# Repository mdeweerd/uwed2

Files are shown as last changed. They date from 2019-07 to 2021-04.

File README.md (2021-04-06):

# WARNING

Project not tested.

# INFORMATION

This is based on the open-source project "Open-Source Potentiostat
for Wireless Electrochemical Detection with Smartphones" 
=
See : https://dash.harvard.edu/bitstream/handle/1/37298552/5997382.pdf;jsessionid=20A09C47E57A66C76ECFA98192F31BF9?sequence=1

The reference to "UWED, Alar Ainla, GMW Group Harvard Univ" was left on the PCB.  They did not design this one, but it was adapted from their Eagle Project.

- The wireless module was replaced with an ESP-WROOM-32 because the original module is no longer supported.
- A programming connector was added.
- A THT connector has been added for power.
- A "Battery Management" IC was added to safely charge a Li-Ion/Li-Poly on power connector.
- There was a project to ajust the PAD positions to a Molex/1719730004

And some other "minor" changes as well as an effort to improve the ground plaine.

# SOFTWARE

See ac8b00850_si_002.zip from https://www.ncbi.nlm.nih.gov/pmc/articles/PMC5997382/ to get the original software as well as further information about this project.

The software has to be adapted to the ESP-WROOM-32.

# BUYING COMPONENTS

The original project ensured that all components were available from Digikey.

The `UWED2_proto.xls` file shows where these components were available in 2019.

At that time you would have been able to paste the following list on https://www.digikey.com/ordering/shoppingcart, but the BOM needs to be updated for some passive components and the ESP-WROOM-32 (was: 1904-1010-1-ND):
```csv
2,401-1427-1-ND,BOOT1;EN1
6,490-3340-2-ND,C1;C2;C5;C6;C16;C18
2,311-1136-1-ND,C10;C12
2,399-16641-1-ND,C20;C21
2,1276-1300-1-ND,C3;C4
9,478-1395-1-ND,C7-C9;C11;C13-C15;C17;C19
1,497-18870-1-ND,D7
1,1904-1010-1-ND,IC1
1,AD5667RBRMZ-2-ND,IC2
1,AD8608ARUZ-ND,IC3
2,576-1259-1-ND,IC4;IC5
1,MAX4643EUA+-ND,IC6
1,MAX4644EUT+TCT-ND,IC7
1,LTC2471IMS#PBF-ND,IC8
1,VAOL-S8SB4CT-ND,LED1
1,CP-032HPJCT-ND,P1
1,GH7540CT-ND,P2
1,RR12P1.2KDCT-ND,R1
2,541-4163-1-ND,R11;R12
2,A130132CT-ND,R14;R15
1,311-16.2KCRCT-ND,R2
2,311-845CRCT-ND,R3;R10
1,311-29.4KCRCT-ND,R4
1,311-8.06KCRCT-ND,R5
1,541-4126-1-ND,R7
3,541-4164-1-ND,R8;R9;R13
```

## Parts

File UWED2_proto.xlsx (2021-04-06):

Prj: | UWED.xml |  |  |  |  |  |  |  |  |  |  | Board Qty: | 1
Co.: |  |  |  |  |  |  |  |  |  |  |  | Unit Cost: | €33.98
Prj date: | 21/04/2019 23:56:42 |  |  |  |  |  |  |  |  |  |  | Total Cost: | €33.98 |  |  |  | €23.32 | 19 of 26 parts found |  |  |  | €42.03 | 26 of 26 parts found |  |  |  | €27.24 | 13 of 26 parts found |  |  |  | €36.15 | 23 of 26 parts found |  |  |  | €10.03 | 17 of 26 parts found |  |  |  | €2531.88 | 7 of 26 parts found |  |  |  | €8.20 | 8 of 26 parts found
$ date: | 2019-04-21 23:56:56
Global Part Info |  |  |  |  |  |  |  |  |  |  |  |  |  | Arrow |  |  |  |  | Digi-Key |  |  |  |  | Farnell |  |  |  |  | Mouser |  |  |  |  | Newark |  |  |  |  | Rs Components |  |  |  |  | Tme
Refs | Value | Desc | S1MN | S1PN | S2PN | S2MN | comment | Footprint | Manf | Manf# | Qty | Unit$ | Ext$ | Avail | Purch | Unit$ | Ext$ | Cat# | Avail | Purch | Unit$ | Ext$ | Cat# | Avail | Purch | Unit$ | Ext$ | Cat# | Avail | Purch | Unit$ | Ext$ | Cat# | Avail | Purch | Unit$ | Ext$ | Cat# | Avail | Purch | Unit$ | Ext$ | Cat# | Avail | Purch | Unit$ | Ext$ | Cat#
BOOT1,EN1 | KMR221G LFS | Microminiature SMT Switch |  |  |  |  |  | Buttons_Switches_SMD:SW_SPST_KMR2 | C&K Components | KMR221G LFS (http://www.mouser.com/ds/2/60/kmr2-1109400.pdf) | 2 | €0.20 | €0.40 | 37333 |  | €0.31 | €0.61 | KMR221G LFS (https://octopart.com/click/track?ak=&sig=092a967&sid=1106&ppid=7484007&vpid=473168312&ct=offers) | 93881 | 2 | €0.52 | €1.04 | 401-1427-1-ND (https://octopart.com/click/track?ak=&sig=0c11080&sid=459&ppid=4774225&vpid=34440877&ct=offers) | NonStk |  | €0.37 | €0.73 | 1201424RL (https://octopart.com/click/track?c=1&ak=&sig=0b550e2&sid=819&ppid=7484007&vpid=138698732&ct=offers) | 47995 |  | €0.52 | €1.04 | 611-KMR221G-LFS (https://octopart.com/click/track?ak=&sig=044d06e&sid=2401&ppid=4774225&vpid=476979092&ct=offers) | 3479 |  | €0.20 | €0.40 | 01M8082 (https://octopart.com/click/track?ak=&sig=005da93&sid=2402&ppid=7484007&vpid=11347265&ct=offers) | 2 |  | €1257.49 | €2514.99 | 1359079 (https://octopart.com/click/track?ak=&sig=023d798&sid=10022&ppid=7484007&vpid=445740908&ct=offers)
C1,C2,C5,C6,C16,C18 | 10u | CAP 10u 0805 |  |  |  |  |  | UWED:C0805 | Murata Electronics | GRM219R60J106KE19D (http://datasheet.octopart.com/GRM219R60J106KE19D-Murata-datasheet-10025737.pdf) | 6 | €0.06 | €0.37 | 1250 |  | €0.29 | €1.72 | GRM219R60J106KE19D (https://octopart.com/click/track?ak=&sig=0b1ee93&sid=1106&ppid=196959&vpid=473333448&ct=offers) | NonStk | 6 | €0.06 | €0.37 | 490-3340-2-ND (https://octopart.com/click/track?c=1&ak=&sig=00207e4&sid=459&ppid=196959&vpid=1720932&ct=offers) | NonStk |  | €0.36 | €2.15 | 1845738 (https://octopart.com/click/track?c=1&ak=&sig=07d642b&sid=819&ppid=196959&vpid=139138268&ct=offers) |  |  |  |  |  | NonStk |  |  |  | 13T1205 (https://octopart.com/click/track?c=1&ak=&sig=093089c&sid=2402&ppid=196959&vpid=33412387&ct=offers) |  |  |  |  |  | 19150 |  | €0.29 | €1.77 | GRM219R60J106KE19D (https://octopart.com/click/track?ak=&sig=0f77df8&sid=1532&ppid=196959&vpid=419362567&ct=offers)
C10,C12 | 10n | CAP 10n 0805 |  |  |  |  |  | UWED:C0805 | Yageo | CC0805KRX7R9BB103 (http://datasheet.octopart.com/CC0805KRX7R9BB103-Yageo-datasheet-10883670.pdf) | 2 | €0.03 | €0.06 | 3872 |  | €0.10 | €0.20 | CC0805KRX7R9BB103 (https://octopart.com/click/track?ak=&sig=0ae48fd&sid=1106&ppid=192989&vpid=486423584&ct=offers) | 8428569 | 2 | €0.11 | €0.22 | 311-1136-1-ND (https://octopart.com/click/track?ak=&sig=0c75d82&sid=459&ppid=192989&vpid=115263416&ct=offers) | 82063 |  | €0.06 | €0.12 | 3019937 (https://octopart.com/click/track?ak=&sig=0170063&sid=819&ppid=192989&vpid=508509172&ct=offers) | 1225222 |  | €0.12 | €0.24 | 603-CC805KRX7R9BB103 (https://octopart.com/click/track?ak=&sig=050a8fd&sid=2401&ppid=192989&vpid=115540545&ct=offers) | 13038 |  | €0.15 | €0.30 | 69C9530 (https://octopart.com/click/track?ak=&sig=0896e52&sid=2402&ppid=192989&vpid=115423638&ct=offers) | 28350 |  | €0.06 | €0.11 | 4614013 (https://octopart.com/click/track?ak=&sig=030c7d2&sid=10022&ppid=192989&vpid=229330082&ct=offers) | 249600 |  | €0.03 | €0.06 | CC0805KRX7R9103 (https://octopart.com/click/track?ak=&sig=0c3fc11&sid=1532&ppid=192989&vpid=115817650&ct=offers)
C20,C21 | 1n | CAP 1n 0805 |  |  |  |  |  | UWED:C0805 | KEMET | C0805C102KARACAUTO (http://datasheet.octopart.com/C0805C102KARACAUTO-KEMET-datasheet-104412711.pdf) | 2 | €0.24 | €0.48 | 7575 |  | €0.27 | €0.53 | C0805C102KARACAUTO (https://octopart.com/click/track?ak=&sig=0f82d17&sid=1106&ppid=88181851&vpid=507223026&ct=offers) | 48644 | 2 | €0.24 | €0.48 | 399-16641-1-ND (https://octopart.com/click/track?ak=&sig=09f6ac1&sid=459&ppid=88181851&vpid=459932081&ct=offers) | 3130 |  | €0.24 | €0.48 | 2834506 (https://octopart.com/click/track?ak=&sig=0deef06&sid=819&ppid=88181851&vpid=477257990&ct=offers) | 9930 |  | €0.28 | €0.56 | 80-C0805C102KARAUTO (https://octopart.com/click/track?ak=&sig=051d296&sid=2401&ppid=88181851&vpid=456357008&ct=offers)
C3,C4 | 470p | CAP 470p 0805 |  |  |  |  |  | UWED:C0805 | Samsung Electro-Mechanics | CL21B471KBANNNC (http://datasheet.octopart.com/CL21B471KBANNNC-Samsung-Electro-Mechanics-datasheet-8324245.pdf) | 2 | €0.01 | €0.02 | 1880 |  | €0.09 | €0.19 | CL21B471KBANNNC (https://octopart.com/click/track?ak=&sig=0d22747&sid=1106&ppid=9301762&vpid=486018211&ct=offers) | 212798 | 2 | €0.10 | €0.20 | 1276-1300-1-ND (https://octopart.com/click/track?ak=&sig=0597cd7&sid=459&ppid=9301762&vpid=72526539&ct=offers) |  |  |  |  |  |  |  |  |  |  |  |  |  |  |  | NonStk |  | €0.01 | €0.02 | 7665950 (https://octopart.com/click/track?c=1&ak=&sig=06b5c12&sid=10022&ppid=9301762&vpid=199121410&ct=offers) | 113900 |  | €0.03 | €0.05 | CL21B471KBANNNC (https://octopart.com/click/track?ak=&sig=0ed60ea&sid=1532&ppid=9301762&vpid=88731159&ct=offers)
C7-C9,C11,C13-C15,C17,C19 | 100n | CAP 100n 0805 |  |  |  |  |  | UWED:C0805 | AVX Corporation | 08055C104KAT2A (http://datasheet.octopart.com/08055C104KAT2A-AVX-datasheet-12587061.pdf) | 9 | €0.02 | €0.22 | 2992000 |  | €0.02 | €0.22 | 08055C104KAT2A (https://octopart.com/click/track?ak=&sig=076accc&sid=1106&ppid=55386349&vpid=527050973&ct=offers) | 47595651 | 9 | €0.18 | €1.62 | 478-1395-1-ND (https://octopart.com/click/track?ak=&sig=01b1845&sid=459&ppid=55386349&vpid=187969502&ct=offers) | NonStk |  | €0.18 | €1.59 | 499687 (https://octopart.com/click/track?c=1&ak=&sig=05bafdf&sid=819&ppid=55386349&vpid=202984868&ct=offers) | NonStk |  | €0.19 | €1.71 | 581-08055C104K (https://octopart.com/click/track?c=1&ak=&sig=0e4db2d&sid=2401&ppid=55386349&vpid=187733814&ct=offers) | NonStk |  | €0.19 | €1.71 | 19X2259 (https://octopart.com/click/track?c=1&ak=&sig=090e783&sid=2402&ppid=55386349&vpid=191188899&ct=offers) | 44500 |  | €0.13 | €1.20 | 4646688 (https://octopart.com/click/track?ak=&sig=082b5da&sid=10022&ppid=55386349&vpid=198971583&ct=offers) | NonStk |  | €0.08 | €0.74 | 08055C104KAT2A (https://octopart.com/click/track?ak=&sig=0e9bd19&sid=1532&ppid=55386349&vpid=187735344&ct=offers)
D7 | STPS2L40AF | DIODE SCHOTTKY 40V 2A SMAFLAT |  |  |  |  |  | Diodes_SMD:D_SMA | STMicroelectronics | STPS2L40AF (http://www.jameco.com/Jameco/Products/ProdDS/1538777.pdf) | 1 | €0.15 | €0.15 | 8 |  | €0.37 | €0.37 | STPS2L40AF (https://octopart.com/click/track?ak=&sig=025aeda&sid=1106&ppid=15756178&vpid=473424643&ct=offers) | 10000 | 1 | €0.44 | €0.44 | 497-18870-1-ND (https://octopart.com/click/track?ak=&sig=075f15a&sid=459&ppid=15756178&vpid=533112807&ct=offers) |  |  |  |  |  | 18242 |  | €0.42 | €0.42 | 511-STPS2L40AF (https://octopart.com/click/track?ak=&sig=01766ab&sid=2401&ppid=15756178&vpid=46230308&ct=offers) | 110000 |  | €0.15 | €0.15 | 96AC4092 (https://octopart.com/click/track?ak=&sig=0df9935&sid=2402&ppid=15756178&vpid=530872283&ct=offers)
IC1 | ESP32-WROOM-32 | SMD MODULE, ESP32-D0WDQ6, 32MBIT |  |  |  |  |  | digikey-footprints:ESP32-WROOM-32D | Espressif Systems | ESP32-WROOM-32 (https://www.espressif.com/sites/default/files/documentation/esp32-wroom-32_datasheet_en.pdf) | 1 | €3.80 | €3.80 |  |  |  |  |  | 1498 | 1 | €3.80 | €3.80 | 1904-1010-1-ND (https://octopart.com/click/track?c=1&ak=&sig=04c9fe0&sid=459&ppid=91025511&vpid=475661582&ct=offers) |  |  |  |  |  | 51941 |  | €3.80 | €3.80 | 356-ESP-WROOM-32 (https://octopart.com/click/track?ak=&sig=0026b78&sid=2401&ppid=91025511&vpid=480613118&ct=offers)
IC2 | DAC_AD5667RBRMZ-2 | Dual DAC. 16-bit I2C |  |  |  |  |  | UWED:MSOP10_0.5MM | Analog Devices | AD5667RBRMZ-2 (http://datasheet.octopart.com/AD5667RBRMZ-2-Analog-Devices-datasheet-124928.pdf) | 1 | €9.91 | €9.91 | 66 |  | €9.91 | €9.91 | AD5667RBRMZ-2 (https://octopart.com/click/track?ak=&sig=03ec865&sid=1106&ppid=1256714&vpid=473140498&ct=offers) | 3052 | 1 | €11.15 | €11.15 | AD5667RBRMZ-2-ND (https://octopart.com/click/track?ak=&sig=049c553&sid=459&ppid=1256714&vpid=1403056&ct=offers) | 167 |  | €11.19 | €11.19 | 1498716 (https://octopart.com/click/track?ak=&sig=02575de&sid=819&ppid=1256714&vpid=138551615&ct=offers) | 182 |  | €10.45 | €10.45 | 584-AD5667RBRMZ-2 (https://octopart.com/click/track?ak=&sig=07a096d&sid=2401&ppid=1256714&vpid=76856573&ct=offers) |  |  |  |  |  | 51 |  | €10.50 | €10.50 | 7590822 (https://octopart.com/click/track?ak=&sig=08808dc&sid=10022&ppid=1256714&vpid=202870150&ct=offers)
IC3 | 4OPAMPS-AD8608ARUZ | QUAD OPAMP |  |  |  |  |  | UWED:MSOP14_0.65MM | Analog Devices | AD8608ARUZ (http://datasheet.octopart.com/AD8608ARUZ-Analog-Devices-datasheet-5333916.pdf) | 1 | €4.29 | €4.29 | 3277 |  | €4.29 | €4.29 | AD8608ARUZ (https://octopart.com/click/track?ak=&sig=0180f02&sid=1106&ppid=412514&vpid=476983376&ct=offers) | 34822 | 1 | €4.87 | €4.87 | AD8608ARUZ-ND (https://octopart.com/click/track?ak=&sig=057ea3f&sid=459&ppid=412514&vpid=1573362&ct=offers) | NonStk |  | €5.16 | €5.16 | 1660999 (https://octopart.com/click/track?c=1&ak=&sig=054ff64&sid=819&ppid=412514&vpid=138558174&ct=offers) | 5478 |  | €4.59 | €4.59 | 584-AD8608ARUZ (https://octopart.com/click/track?ak=&sig=01a240d&sid=2401&ppid=412514&vpid=77165439&ct=offers) |  |  |  |  |  | 18 |  | €4.38 | €4.38 | 412917 (https://octopart.com/click/track?ak=&sig=06e1585&sid=10022&ppid=412514&vpid=202871180&ct=offers) | 5 |  | €4.38 | €4.38 | AD8608ARUZ (https://octopart.com/click/track?ak=&sig=00dbee1&sid=1532&ppid=412514&vpid=431488339&ct=offers)
IC4,IC5 | LDO-MIC5205-3.3YM5-TR | LDO 3V3 |  |  |  |  |  | UWED:SOT-23-6 | Micron | MIC5205-3.3YM5-TR (http://datasheet.octopart.com/MIC5205-3.3YM5-TR-Microchip-datasheet-3438.pdf) | 2 | €0.33 | €0.67 | 1792 |  | €0.37 | €0.74 | MIC5205-3.3YM5-TR (https://octopart.com/click/track?ak=&sig=0130a16&sid=1106&ppid=66802130&vpid=473300413&ct=offers) | 13459 | 2 | €0.41 | €0.82 | 576-1259-1-ND (https://octopart.com/click/track?ak=&sig=013f1bc&sid=459&ppid=66802130&vpid=240151191&ct=offers) | 8674 |  | €0.40 | €0.80 | 2510222 (https://octopart.com/click/track?ak=&sig=0dd40c3&sid=819&ppid=66802130&vpid=250077688&ct=offers) | 14944 |  | €0.41 | €0.82 | 998-MIC5205-3.3YM5TR (https://octopart.com/click/track?ak=&sig=0603f47&sid=2401&ppid=66802130&vpid=241196800&ct=offers) | 6200 |  | €0.38 | €0.77 | 77Y7676 (https://octopart.com/click/track?ak=&sig=0f9fff7&sid=2402&ppid=66802130&vpid=252553478&ct=offers) | 1550 |  | €0.33 | €0.67 | 9101556 (https://octopart.com/click/track?ak=&sig=0bacc1a&sid=10022&ppid=66802130&vpid=277370722&ct=offers) | 295 |  | €0.54 | €1.08 | MIC5205-3.3YM5-TR (https://octopart.com/click/track?ak=&sig=0a90aa9&sid=1532&ppid=66802130&vpid=430922300&ct=offers)
IC6 | SWITCH_MAX4643EUA | Dual switch |  |  |  |  |  | UWED:MSOP8_0.65MM | Maxim | MAX4643EUA+ (http://datasheet.octopart.com/MAX4643EUA-Maxim-datasheet-132654.pdf) | 1 | €1.59 | €1.59 |  |  |  |  |  | 270 | 1 | €1.62 | €1.62 | MAX4643EUA+-ND (https://octopart.com/click/track?ak=&sig=0bca648&sid=459&ppid=42454999&vpid=116452538&ct=offers) | NonStk |  | €1.59 | €1.59 | 2513055 (https://octopart.com/click/track?c=1&ak=&sig=0afb6d2&sid=819&ppid=42454999&vpid=247811369&ct=offers) | 237 |  | €1.62 | €1.62 | 700-MAX4643EUA (https://octopart.com/click/track?ak=&sig=03a5efa&sid=2401&ppid=42454999&vpid=118374851&ct=offers) | NonStk |  |  |  | 73Y4402 (https://octopart.com/click/track?c=1&ak=&sig=09888c9&sid=2402&ppid=42454999&vpid=252535778&ct=offers)
IC7 | SWITCH_MAX4644EUT | Single switch |  |  |  |  |  | UWED:SOT-23-6 | Maxim | MAX4644EUT+T (http://datasheet.octopart.com/MAX4644EUT-T-Maxim-datasheet-124824.pdf) | 1 | €2.08 | €2.08 |  |  |  |  |  | 8226 | 1 | €2.98 | €2.98 | MAX4644EUT+TCT-ND (https://octopart.com/click/track?ak=&sig=0cc4e45&sid=459&ppid=39581104&vpid=115220404&ct=offers) | 556 |  | €2.94 | €2.94 | 2513217 (https://octopart.com/click/track?ak=&sig=027b1ae&sid=819&ppid=39581104&vpid=247811371&ct=offers) | 2614 |  | €2.98 | €2.98 | 700-MAX4644EUTT (https://octopart.com/click/track?ak=&sig=0475005&sid=2401&ppid=39581104&vpid=116509793&ct=offers) | 904 |  | €2.08 | €2.08 | 73Y4404 (https://octopart.com/click/track?ak=&sig=0bbf81e&sid=2402&ppid=39581104&vpid=252535784&ct=offers)
IC8 | ADC_LTC2471IMS | 16-bit ADC, I2C |  |  |  |  |  | UWED:MSOP12_0.65MM | Analog Devices | LTC2471IMS#PBF (http://datasheet.octopart.com/LTC2471IMS%23PBF-Linear-Technology-datasheet-17726001.pdf) | 1 | €4.72 | €4.72 |  |  |  |  |  | 401 | 1 | €4.72 | €4.72 | LTC2471IMS#PBF-ND (https://octopart.com/click/track?c=1&ak=&sig=03e7092&sid=459&ppid=19077751&vpid=33773660&ct=offers)
LED1 | LED (blue) | Led Blue Clear 0805 |  |  |  |  |  | UWED:SML0805 | Visual Communications Company - VCC | VAOL-S8SB4 (http://datasheet.octopart.com/VAOL-S8SB4-VCC-datasheet-8502562.pdf) | 1 | €0.32 | €0.32 | 22 |  | €0.32 | €0.32 | VAOL-S8SB4 (https://octopart.com/click/track?ak=&sig=080c203&sid=1106&ppid=11855049&vpid=473518303&ct=offers) | 5450 | 1 | €0.47 | €0.47 | VAOL-S8SB4CT-ND (https://octopart.com/click/track?ak=&sig=0603068&sid=459&ppid=11855049&vpid=97283745&ct=offers) | 5706 |  | €0.35 | €0.35 | 2748714 (https://octopart.com/click/track?ak=&sig=03e9390&sid=819&ppid=11855049&vpid=465006215&ct=offers) | 2832 |  | €0.34 | €0.34 | 593-VAOL-S8SB4 (https://octopart.com/click/track?ak=&sig=0b3fcf6&sid=2401&ppid=11855049&vpid=37785716&ct=offers) | 3348 |  | €0.34 | €0.34 | 27R0109 (https://octopart.com/click/track?ak=&sig=00dcaeb&sid=2402&ppid=11855049&vpid=20231201&ct=offers)
P1 | PJ-032H-SMT-TR | Jack 0.7x2.35mm |  |  |  |  |  | UWED:PJ-032H-SMT | CUI Inc. | PJ-032H-SMT-TR (http://datasheet.octopart.com/PJ-032H-SMT-TR-CUI-datasheet-100142472.pdf) | 1 | €0.95 | €0.95 |  |  |  |  |  | 5418 | 1 | €1.05 | €1.05 | CP-032HPJCT-ND (https://octopart.com/click/track?ak=&sig=05e8df8&sid=459&ppid=25947168&vpid=63783277&ct=offers) |  |  |  |  |  | 1324 |  | €0.95 | €0.95 | 490-PJ-032H-SMT-TR (https://octopart.com/click/track?ak=&sig=095fc16&sid=2401&ppid=25947168&vpid=220342292&ct=offers)
P2 | 34EWMSP12M6RT | Toggle Switch SPDT Surface Mount, Right Angle |  |  |  |  |  | UWED:TOGGLE_34E | Grayhill Inc. | 34EWMSP12M6RT (http://datasheet.octopart.com/34EWMSP12M6RT-Grayhill-datasheet-11839840.pdf) | 1 | €3.81 | €3.81 | 914 |  | €3.81 | €3.81 | 34EWMSP12M6RT (https://octopart.com/click/track?ak=&sig=00992e8&sid=1106&ppid=90738&vpid=473220208&ct=offers) | 1942 | 1 | €4.77 | €4.77 | GH7540CT-ND (https://octopart.com/click/track?ak=&sig=0ddba23&sid=459&ppid=90738&vpid=40829069&ct=offers) |  |  |  |  |  | 55 |  | €5.00 | €5.00 | 706-34EWMSP12M6RT (https://octopart.com/click/track?ak=&sig=0b1f9bc&sid=2401&ppid=90738&vpid=114471257&ct=offers) | 1342 |  | €4.06 | €4.06 | 13N5692 (https://octopart.com/click/track?ak=&sig=0ff94a4&sid=2402&ppid=90738&vpid=30137956&ct=offers)
R1 | 1k2 | RES 1K2 0806 |  |  |  |  |  | UWED:R0805 | Susumu | RR1220P-122-D (http://datasheet.octopart.com/RR1220P-122-D-Susumu-datasheet-5302462.pdf) | 1 | €0.01 | €0.01 |  |  |  |  |  | 16849 | 1 | €0.11 | €0.11 | RR12P1.2KDCT-ND (https://octopart.com/click/track?ak=&sig=0d43023&sid=459&ppid=981665&vpid=1230012&ct=offers) | 3687 |  | €0.10 | €0.10 | 9369937 (https://octopart.com/click/track?ak=&sig=09b411a&sid=819&ppid=981665&vpid=139693991&ct=offers) | 10232 |  | €0.10 | €0.10 | 754-RR1220P-122D (https://octopart.com/click/track?ak=&sig=050dae0&sid=2401&ppid=981665&vpid=66948506&ct=offers) | 3687 |  | €0.01 | €0.01 | 28K0960 (https://octopart.com/click/track?ak=&sig=0984767&sid=2402&ppid=981665&vpid=2942973&ct=offers) | 5400 |  |  |  | 6019202P (https://octopart.com/click/track?ak=&sig=0f91073&sid=10022&ppid=981665&vpid=168877474&ct=offers)
R11,R12 | 10k | RES 10K 0806 |  |  |  |  |  | UWED:R0805 | Vishay Dale | CRCW080510K0JNEAC | 2 | €0.004 | €0.01 | 282260 |  | €0.004 | €0.01 | CRCW080510K0JNEAC (https://octopart.com/click/track?ak=&sig=08c7d26&sid=1106&ppid=22248114&vpid=477979982&ct=offers) | 141618 | 2 | €0.10 | €0.20 | 541-4163-1-ND (https://octopart.com/click/track?ak=&sig=0e3dded&sid=459&ppid=22248114&vpid=454353709&ct=offers) |  |  |  |  |  | 75173 |  | €0.10 | €0.20 | 71-CRCW080510K0JNEAC (https://octopart.com/click/track?ak=&sig=0e7bfa5&sid=2401&ppid=22248114&vpid=458953937&ct=offers) | 10000 |  | €0.03 | €0.05 | 98AC1023 (https://octopart.com/click/track?ak=&sig=04b390a&sid=2402&ppid=22248114&vpid=532301088&ct=offers)
R14,R15 | 470R | RES 470R 0806 |  |  |  |  |  | UWED:R0805 | TE Connectivity | CRGCQ0805J470R (http://sigma.octopart.com/114702769/technical_drawing/TE-Connectivity-CRGCQ0805J470R.pdf) | 2 | €0.0042 | €0.01 | 4980 |  | €0.0042 | €0.01 | CRGCQ0805J470R (https://octopart.com/click/track?ak=&sig=04ea6a4&sid=1106&ppid=91018229&vpid=494397254&ct=offers) | 119990 | 2 | €0.10 | €0.20 | A130132CT-ND (https://octopart.com/click/track?ak=&sig=063e7fc&sid=459&ppid=91018229&vpid=475508919&ct=offers) | 16 |  | €0.02 | €0.03 | 2861905 (https://octopart.com/click/track?ak=&sig=064e05c&sid=819&ppid=91018229&vpid=503455793&ct=offers) | 13516 |  | €0.14 | €0.28 | 279-CRGCQ0805J470R (https://octopart.com/click/track?ak=&sig=00b7193&sid=2401&ppid=91018229&vpid=478301079&ct=offers) | 34 |  | €0.01 | €0.02 | 61AC6636 (https://octopart.com/click/track?ak=&sig=0dde457&sid=2402&ppid=91018229&vpid=503307495&ct=offers)
R2 | 16k2 | RES 16K2 0806 |  |  |  |  |  | UWED:R0805 | Yageo | RC0805FR-0716K2L (http://datasheet.octopart.com/RC0805FR-0716K2L-Yageo-datasheet-127823281.pdf) | 1 | €0.003 | €0.003 | 6237 |  | €0.003 | €0.003 | RC0805FR-0716K2L (https://octopart.com/click/track?ak=&sig=093e727&sid=1106&ppid=39850618&vpid=487639162&ct=offers) | 307334 | 1 | €0.10 | €0.10 | 311-16.2KCRCT-ND (https://octopart.com/click/track?ak=&sig=0412357&sid=459&ppid=39850618&vpid=114983232&ct=offers) |  |  |  |  |  | 101960 |  | €0.13 | €0.13 | 603-RC0805FR-0716K2L (https://octopart.com/click/track?ak=&sig=01b22f1&sid=2401&ppid=39850618&vpid=165627792&ct=offers) | NonStk |  | €0.01 | €0.01 | 66R2982 (https://octopart.com/click/track?c=1&ak=&sig=00bcda1&sid=2402&ppid=39850618&vpid=166707613&ct=offers)
R3,R10 | 845R | RES 845R 0806 |  |  |  |  |  | UWED:R0805 | Yageo | RC0805FR-07845RL (http://datasheet.octopart.com/RC0805FR-07845RL-Yageo-datasheet-118657.pdf) | 2 | €0.01 | €0.02 |  |  |  |  |  | 66537 | 2 | €0.10 | €0.20 | 311-845CRCT-ND (https://octopart.com/click/track?ak=&sig=09ac469&sid=459&ppid=1170020&vpid=1678128&ct=offers) |  |  |  |  |  | 17231 |  | €0.13 | €0.26 | 603-RC0805FR-07845RL (https://octopart.com/click/track?ak=&sig=05ae8ab&sid=2401&ppid=1170020&vpid=198857945&ct=offers) | NonStk |  | €0.01 | €0.02 | 66R3516 (https://octopart.com/click/track?c=1&ak=&sig=043ea6d&sid=2402&ppid=1170020&vpid=96902892&ct=offers) |  |  |  |  |  | 2300 |  | €0.04 | €0.08 | RC0805FR-07845RL (https://octopart.com/click/track?ak=&sig=0150fef&sid=1532&ppid=1170020&vpid=433931373&ct=offers)
R4 | 29k4 | RES 29K4 0806 |  |  |  |  |  | UWED:R0805 | Yageo | RC0805FR-0729K4L (http://datasheet.octopart.com/RC0805FR-0729K4L-Yageo-datasheet-127823281.pdf) | 1 | €0.003 | €0.003 | 16773 |  | €0.003 | €0.003 | RC0805FR-0729K4L (https://octopart.com/click/track?ak=&sig=0ef9bd1&sid=1106&ppid=1204081&vpid=473551303&ct=offers) | 302269 | 1 | €0.10 | €0.10 | 311-29.4KCRCT-ND (https://octopart.com/click/track?ak=&sig=0efb51e&sid=459&ppid=1204081&vpid=1187886&ct=offers) |  |  |  |  |  | 49649 |  | €0.13 | €0.13 | 603-RC0805FR-0729K4L (https://octopart.com/click/track?ak=&sig=012087c&sid=2401&ppid=1204081&vpid=56304309&ct=offers) | NonStk |  | €0.01 | €0.01 | 66R3153 (https://octopart.com/click/track?c=1&ak=&sig=0219af0&sid=2402&ppid=1204081&vpid=96902579&ct=offers) |  |  |  |  |  | 13800 |  | €0.04 | €0.04 | RC0805FR-0729K4L (https://octopart.com/click/track?ak=&sig=0f9bbc7&sid=1532&ppid=1204081&vpid=433931042&ct=offers)
R5 | 8k6 | RES 8K06 0806 |  |  |  |  |  | UWED:R0805 | Yageo | RC0805FR-078K06L (http://datasheet.octopart.com/RC0805FR-078K06L-Yageo-datasheet-118657.pdf) | 1 | €0.0028 | €0.0028 | 5674 |  | €0.0028 | €0.0028 | RC0805FR-078K06L (https://octopart.com/click/track?ak=&sig=0485d57&sid=1106&ppid=1287869&vpid=473551733&ct=offers) | 254536 | 1 | €0.10 | €0.10 | 311-8.06KCRCT-ND (https://octopart.com/click/track?ak=&sig=048b5c5&sid=459&ppid=1287869&vpid=1630312&ct=offers) |  |  |  |  |  | 51819 |  | €0.13 | €0.13 | 603-RC0805FR-078K06L (https://octopart.com/click/track?ak=&sig=0d2ec1a&sid=2401&ppid=1287869&vpid=46088460&ct=offers) | NonStk |  | €0.01 | €0.01 | 66R3485 (https://octopart.com/click/track?c=1&ak=&sig=02b87d2&sid=2402&ppid=1287869&vpid=96902901&ct=offers)
R7 | OR | RES 0R 0806 |  |  |  |  |  | UWED:R0805 | Vishay Dale | CRCW08050000Z0EBC (http://datasheet.octopart.com/CRCW08050000Z0EBC-Vishay-datasheet-100063072.pdf) | 1 | €0.01 | €0.01 | 208 |  | €0.10 | €0.10 | CRCW08050000Z0EBC (https://octopart.com/click/track?ak=&sig=0defb24&sid=1106&ppid=87884302&vpid=482010591&ct=offers) | 199199 | 1 | €0.10 | €0.10 | 541-4126-1-ND (https://octopart.com/click/track?ak=&sig=068a365&sid=459&ppid=87884302&vpid=454353686&ct=offers) |  |  |  |  |  | 92322 |  | €0.10 | €0.10 | 71-CRCW08050000Z0EBC (https://octopart.com/click/track?ak=&sig=0ecee72&sid=2401&ppid=87884302&vpid=458953923&ct=offers) | NonStk |  | €0.01 | €0.01 | 59AC3308 (https://octopart.com/click/track?c=1&ak=&sig=026db87&sid=2402&ppid=87884302&vpid=508831544&ct=offers)
R8,R9,R13 | 100k | RES 100K 0806 |  |  |  |  |  | UWED:R0805 | Vishay Dale | CRCW0805100KJNEAC (http://datasheet.octopart.com/CRCW0805100KJNEAC-Vishay-datasheet-100063072.pdf) | 3 | €0.03 | €0.08 | 17266 |  | €0.10 | €0.29 | CRCW0805100KJNEAC (https://octopart.com/click/track?ak=&sig=0371b33&sid=1106&ppid=23798530&vpid=480316977&ct=offers) | 137370 | 3 | €0.10 | €0.30 | 541-4164-1-ND (https://octopart.com/click/track?ak=&sig=054aca2&sid=459&ppid=23798530&vpid=454353695&ct=offers) |  |  |  |  |  | 35992 |  | €0.10 | €0.30 | 71-CRCW0805100KJNEAC (https://octopart.com/click/track?ak=&sig=09648a2&sid=2401&ppid=23798530&vpid=458953926&ct=offers) | 40000 |  | €0.03 | €0.08 | 95AC8878 (https://octopart.com/click/track?ak=&sig=03fde5c&sid=2402&ppid=23798530&vpid=530876537&ct=offers)
KiCost® v.1.0.5 |  |  |  |  |  |  |  |  |  |  |  | Total Purchase: | €42.03 |  |  |  | €0.00 |  |  | 26 of 26 parts purchased |  | €42.03 |  |  |  |  | €0.00 |  |  |  |  | €0.00 |  |  |  |  | €0.00 |  |  |  |  | €0.00 |  |  |  |  | €0.00
 |  |  |  |  |  |  |  |  |  |  |  |  |  |  |  |  |  |  |  | 2,401-1427-1-ND,BOOT1;EN1
 |  |  |  |  |  |  |  |  |  |  |  |  |  |  |  |  |  |  |  | 6,490-3340-2-ND,C1;C2;C5;C6;C16;C18
 |  |  |  |  |  |  |  |  |  |  |  |  |  |  |  |  |  |  |  | 2,311-1136-1-ND,C10;C12
 |  |  |  |  |  |  |  |  |  |  |  |  |  |  |  |  |  |  |  | 2,399-16641-1-ND,C20;C21
 |  |  |  |  |  |  |  |  |  |  |  |  |  |  |  |  |  |  |  | 2,1276-1300-1-ND,C3;C4
 |  |  |  |  |  |  |  |  |  |  |  |  |  |  |  |  |  |  |  | 9,478-1395-1-ND,C7-C9;C11;C13-C15;C17;C19
 |  |  |  |  |  |  |  |  |  |  |  |  |  |  |  |  |  |  |  | 1,497-18870-1-ND,D7
 |  |  |  |  |  |  |  |  |  |  |  |  |  |  |  |  |  |  |  | 1,1904-1010-1-ND,IC1
 |  |  |  |  |  |  |  |  |  |  |  |  |  |  |  |  |  |  |  | 1,AD5667RBRMZ-2-ND,IC2
 |  |  |  |  |  |  |  |  |  |  |  |  |  |  |  |  |  |  |  | 1,AD8608ARUZ-ND,IC3
 |  |  |  |  |  |  |  |  |  |  |  |  |  |  |  |  |  |  |  | 2,576-1259-1-ND,IC4;IC5
 |  |  |  |  |  |  |  |  |  |  |  |  |  |  |  |  |  |  |  | 1,MAX4643EUA+-ND,IC6
 |  |  |  |  |  |  |  |  |  |  |  |  |  |  |  |  |  |  |  | 1,MAX4644EUT+TCT-ND,IC7
 |  |  |  |  |  |  |  |  |  |  |  |  |  |  |  |  |  |  |  | 1,LTC2471IMS#PBF-ND,IC8
 |  |  |  |  |  |  |  |  |  |  |  |  |  |  |  |  |  |  |  | 1,VAOL-S8SB4CT-ND,LED1
 |  |  |  |  |  |  |  |  |  |  |  |  |  |  |  |  |  |  |  | 1,CP-032HPJCT-ND,P1
 |  |  |  |  |  |  |  |  |  |  |  |  |  |  |  |  |  |  |  | 1,GH7540CT-ND,P2
 |  |  |  |  |  |  |  |  |  |  |  |  |  |  |  |  |  |  |  | 1,RR12P1.2KDCT-ND,R1
 |  |  |  |  |  |  |  |  |  |  |  |  |  |  |  |  |  |  |  | 2,541-4163-1-ND,R11;R12
 |  |  |  |  |  |  |  |  |  |  |  |  |  |  |  |  |  |  |  | 2,A130132CT-ND,R14;R15
 |  |  |  |  |  |  |  |  |  |  |  |  |  |  |  |  |  |  |  | 1,311-16.2KCRCT-ND,R2
 |  |  |  |  |  |  |  |  |  |  |  |  |  |  |  |  |  |  |  | 2,311-845CRCT-ND,R3;R10
 |  |  |  |  |  |  |  |  |  |  |  |  |  |  |  |  |  |  |  | 1,311-29.4KCRCT-ND,R4
 |  |  |  |  |  |  |  |  |  |  |  |  |  |  |  |  |  |  |  | 1,311-8.06KCRCT-ND,R5
 |  |  |  |  |  |  |  |  |  |  |  |  |  |  |  |  |  |  |  | 1,541-4126-1-ND,R7
 |  |  |  |  |  |  |  |  |  |  |  |  |  |  |  |  |  |  |  | 3,541-4164-1-ND,R8;R9;R13

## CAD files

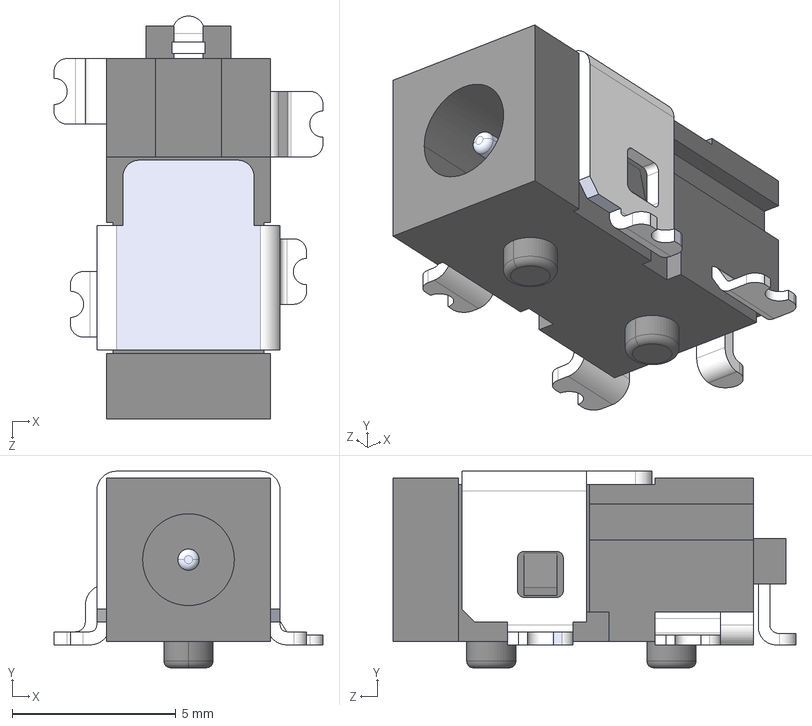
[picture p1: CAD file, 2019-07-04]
3dmodels/CUI_PJ-032H-SMT-TR.step
8.20 x 6.00 x 12.3 mm

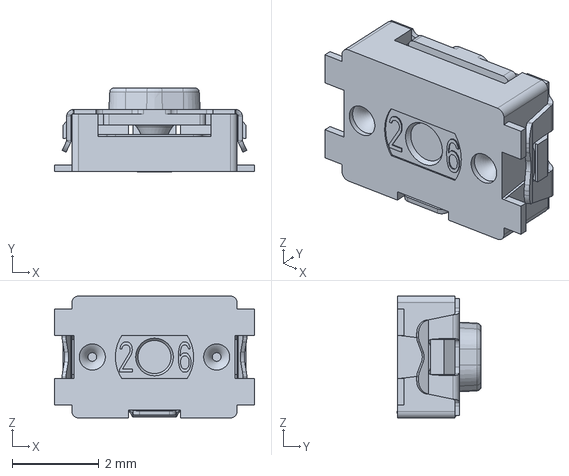
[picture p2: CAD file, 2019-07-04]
3dmodels/KMR221GLFS.stp
4.60 x 1.94 x 2.80 mm

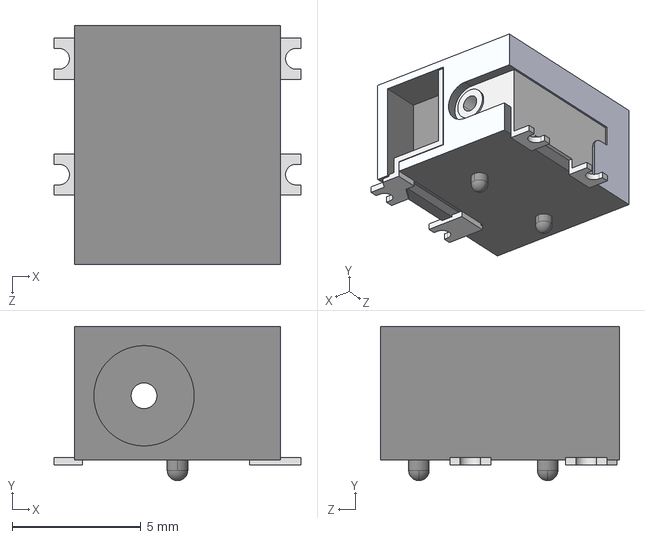
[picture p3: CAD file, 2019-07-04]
3dmodels/CUI_PJ-014CH-SMT-TR.step
9.60 x 6.00 x 9.30 mm

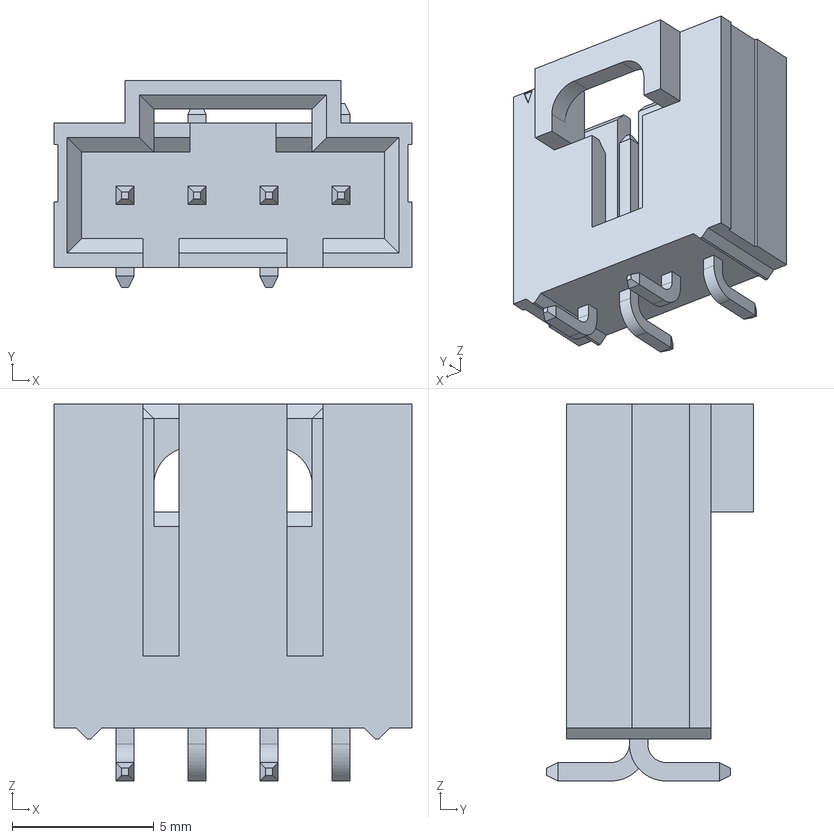
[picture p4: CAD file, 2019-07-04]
3dmodels/1719730004.stp
12.6 x 7.30 x 13.3 mm

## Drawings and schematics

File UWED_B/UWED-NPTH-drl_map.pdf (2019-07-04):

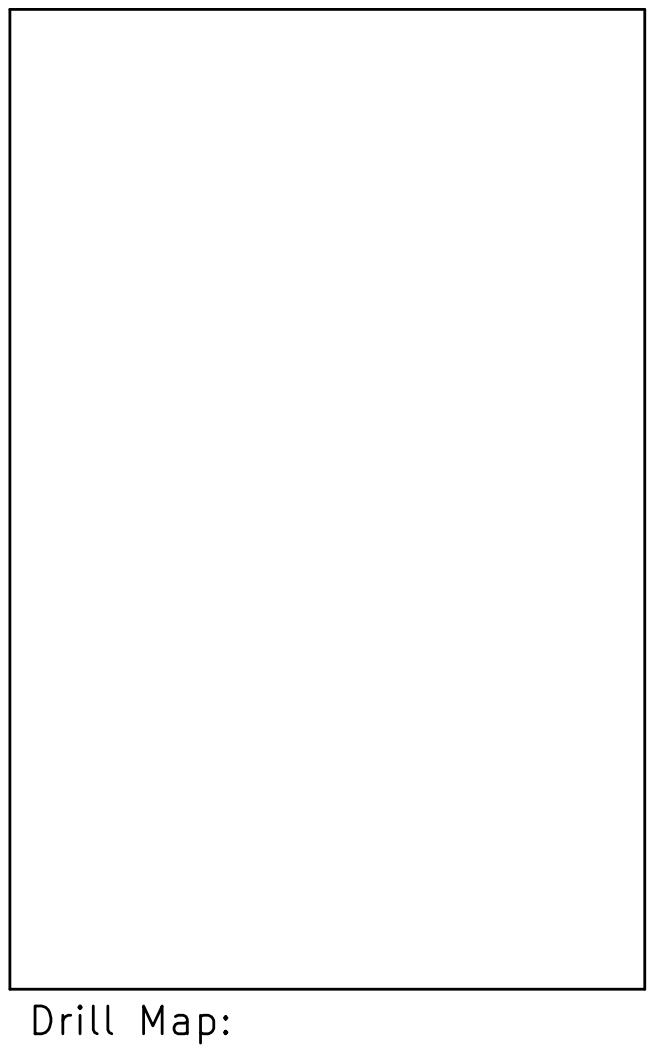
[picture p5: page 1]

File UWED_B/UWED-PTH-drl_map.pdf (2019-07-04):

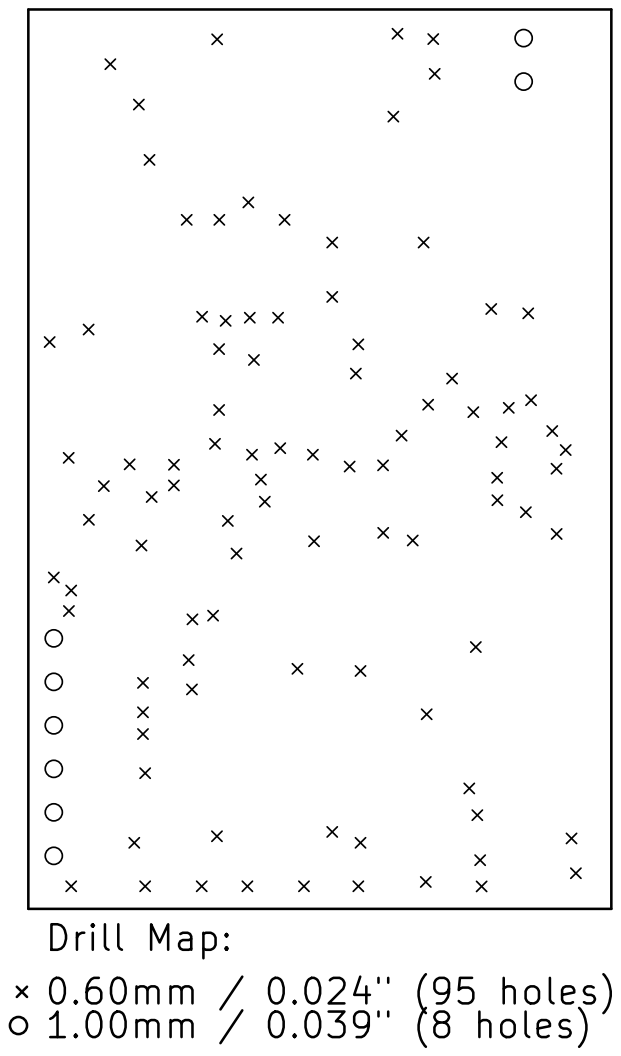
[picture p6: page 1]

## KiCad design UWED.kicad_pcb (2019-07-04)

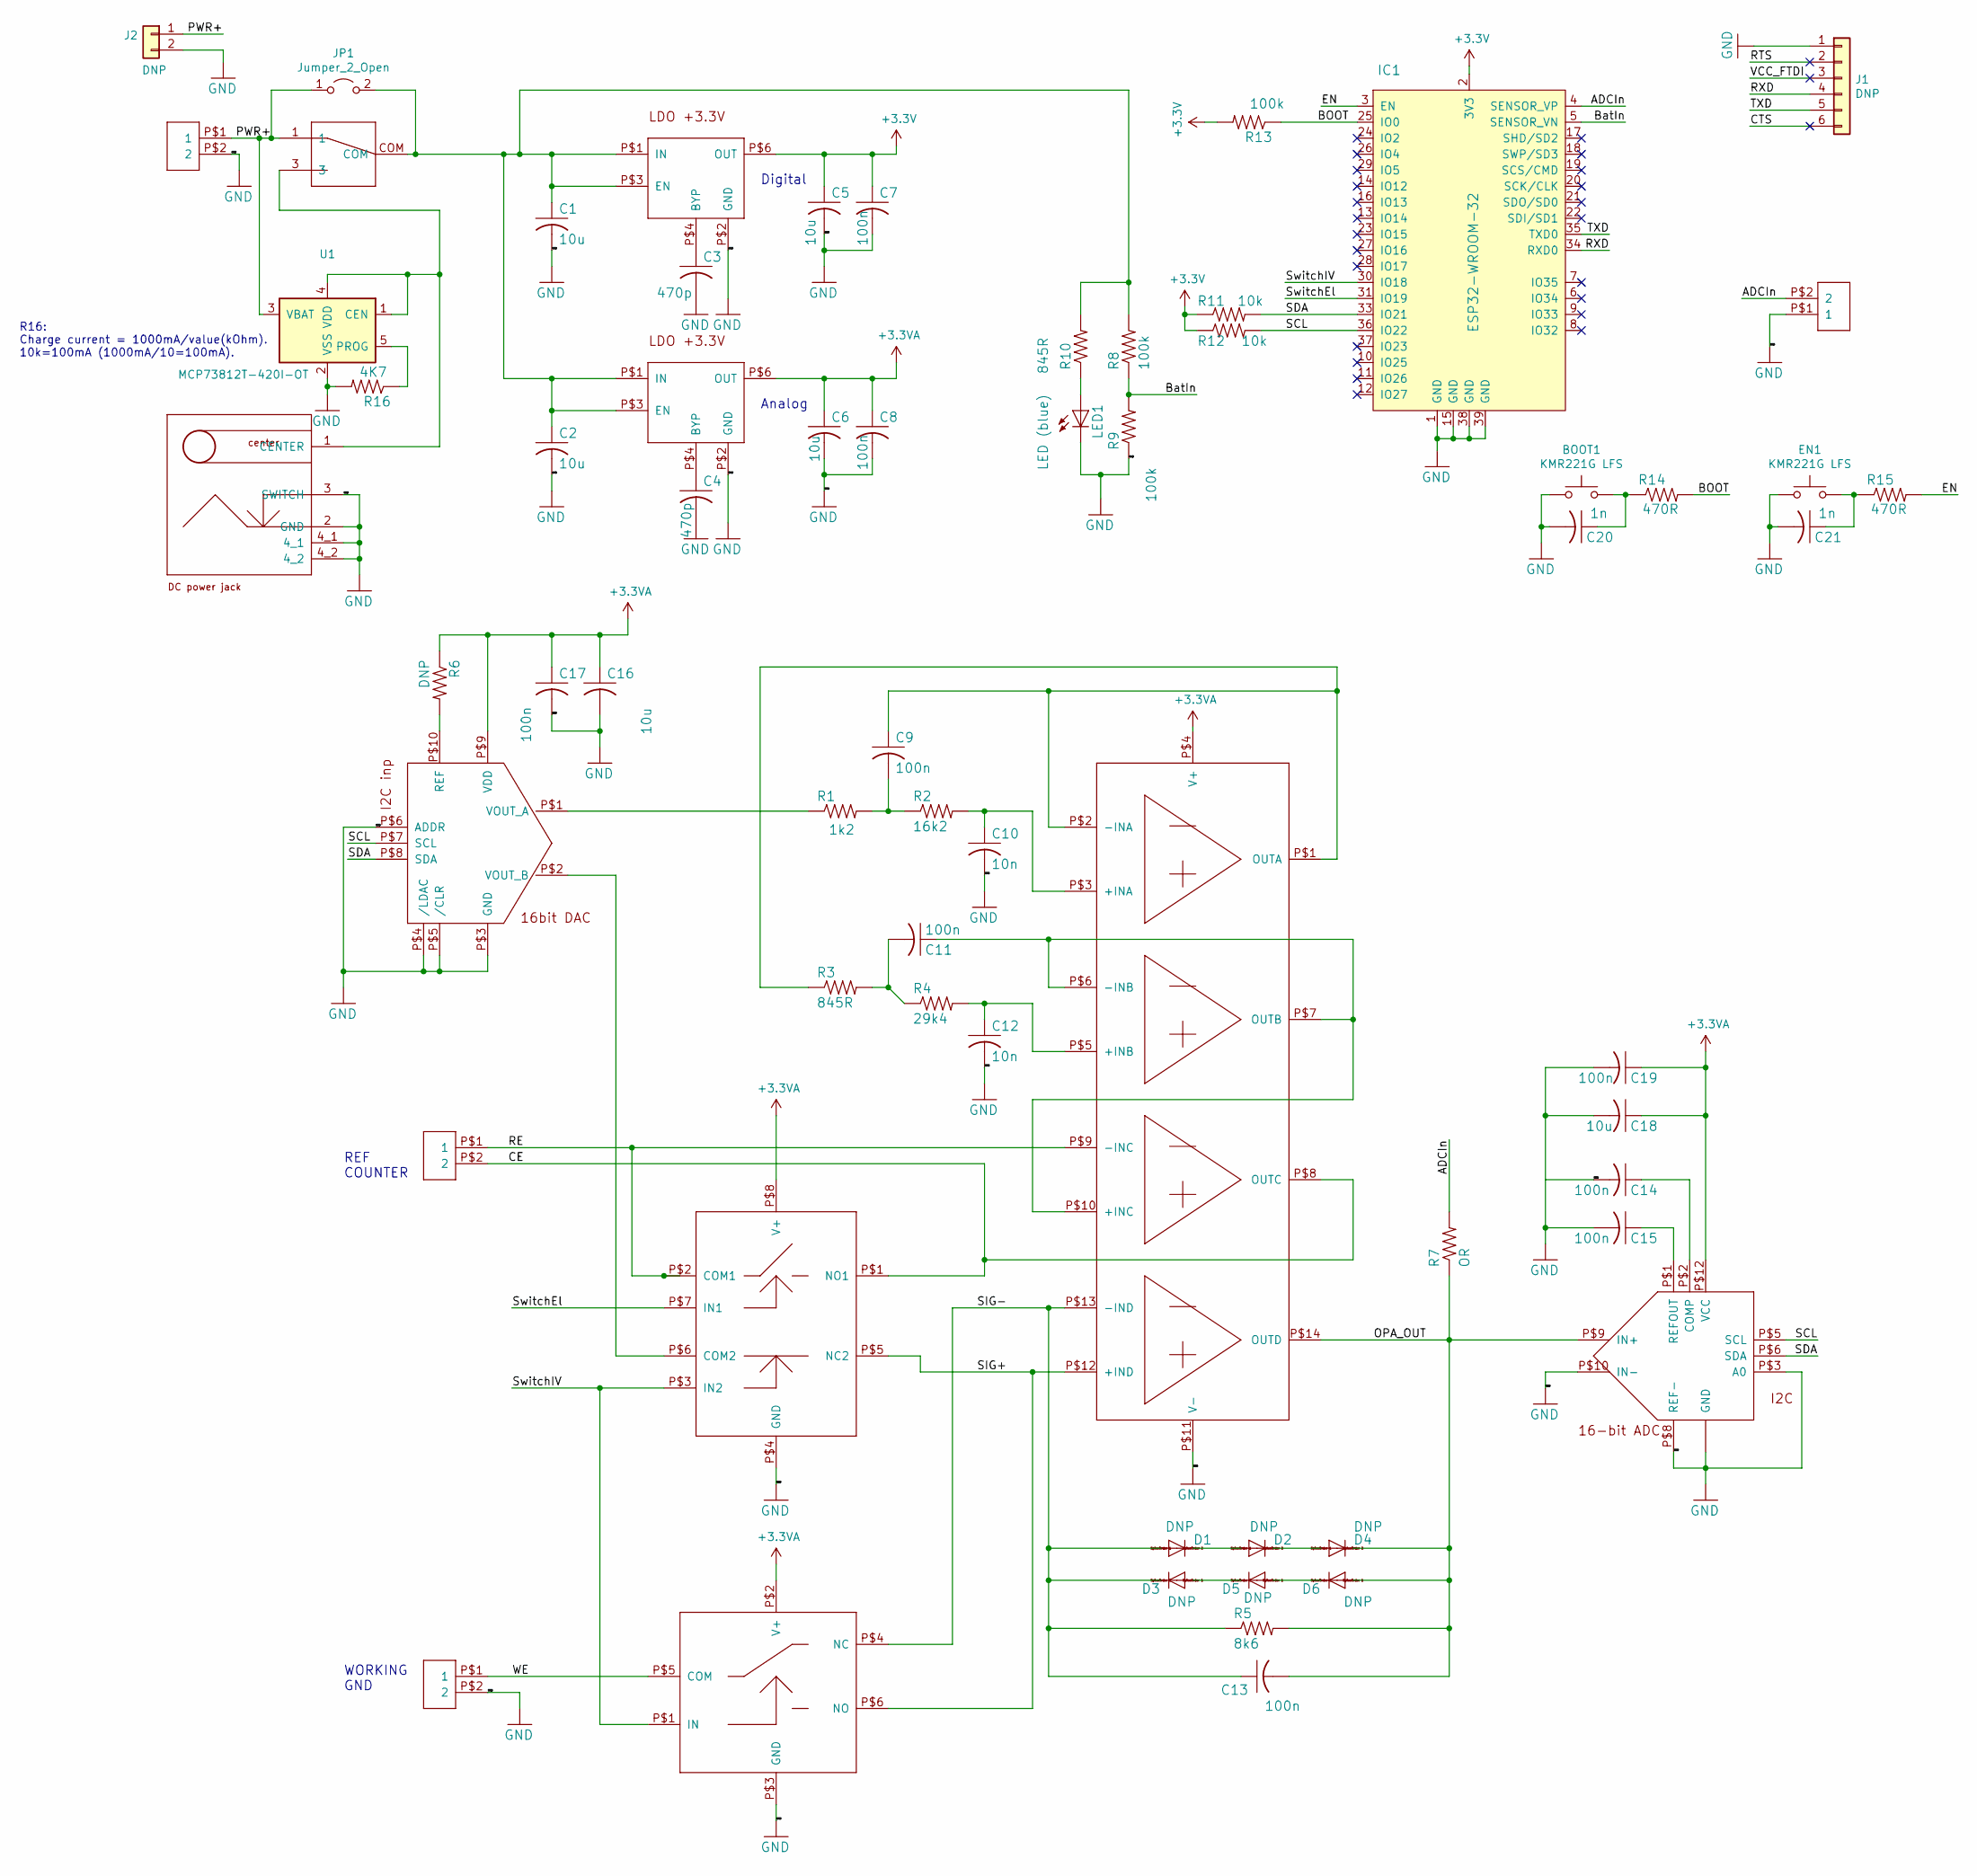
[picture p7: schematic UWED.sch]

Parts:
BOOT1: KMR221G LFS; SW_SPST_KMR2; mouser.manf# 611-KMR221G-LFS
C1, C2, C5, C6, C16, C18: 10u; C0805; digikey.manf# 490-3340-1-ND
C3, C4: 470p; C0805; digikey.manf# 1276-1300-1-ND
C7, C8, C9, C11, C13, C14, C15, C17, C19: 100n; C0805; digikey.manf# 478-1395-1-ND
C10, C12: 10n; C0805; digikey.manf# 311-1136-1-ND
C20, C21: 1n; C0805; digikey.manf# 399-16641-1-ND
D1, D2, D3, D4, D5, D6: DNP; SOD80C
EN1: KMR221G LFS; SW_SPST_KMR2; mouser.manf# 611-KMR221G-LFS
IC1: ESP32-WROOM-32; ESP32-WROOM-32D; MPN ESP32-WROOM-32; digikey.manf# 1904-1010-1-ND
IC2: DAC_AD5667RBRMZ-2; MSOP10_0.5MM; MPN AD5667RBRMZ-2; digikey.manf# AD5667RBRMZ-2-ND
IC3: 4OPAMPS-AD8608ARUZ; MSOP14_0.65MM; MPN AD8608ARUZ; digikey.manf# AD868ARUZ-ND
IC4, IC5: LDO-MIC5205-3.3YM5-TR; SOT-23-6; MPN MIC5205-3.3YM5-TR; digikey.manf# 576-1259-1-ND
IC6: SWITCH_MAX4643EUA; MSOP8_0.65MM; MPN MAX4643EUA+; digikey.manf# MAX4643EUA+-ND
IC7: SWITCH_MAX4644EUT; SOT-23-6; MPN MAX4644EUT+T; digikey.manf# MAX4644EUT+TCTND
IC8: ADC_LTC2471IMS; MSOP12_0.65MM; MPN LTC2471IMS#PBF; digikey.manf# LTC2471IMS#PBFND
J1: DNP; Pin_Header_Straight_1x06_Pitch2.54mm
J2: DNP; Pin_Header_Straight_1x02_Pitch2.54mm
JP1: Jumper_2_Open; SolderJumper-2_P1.3mm_Open_TrianglePad1.0x1.5mm
LED1: LED (blue); SML0805; digikey.manf# VAOL-S8SB4CT-ND
P1: PJ-032H-SMT-TR; PJ-032H-SMT; MPN PJ-032H-SMT-TR; digikey.manf# CP-032HPJCT-ND
P2: 34EWMSP12M6RT; TOGGLE_34E; MPN 34EWMSP12M6RT; digikey.manf# GH7540CT-ND
R1: 1k2; R0805; digikey.manf# RR12P1.2KDCT-ND
R2: 16k2; R0805; digikey.manf# 311-16.2KCRCT-ND
R3, R10: 845R; R0805; digikey.manf# 311-845CRCT-ND
R4: 29k4; R0805; digikey.manf# 311-29.4KCRCT-ND
R5: 8k6; R0805; digikey.manf# 311-8.06KCRCT-ND
R6: DNP; R0805; digikey.manf# 541-4126-1-ND
R7: OR; R0805; digikey.manf# 541-4126-1-ND
R8, R9, R13: 100k; R0805; digikey.manf# 541-4164-1-ND
R11, R12: 10k; R0805; digikey.manf# 541-4163-1-ND
R14, R15: 470R; R0805; digikey.manf# A130132CT-ND
R16: 4K7; R0805; digikey.manf# A130132CT-ND
U1: MCP73812T-420I-OT; SOT-23-5_HandSoldering
U$3, U$6, U$7, U$15: CONTACT_PADS_SMD_2

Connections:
+3.3VA: C6.1, C8.1, C16.1, C17.1, C18.1, C19.1, IC2.P$9 (VDD), IC3.P$4 (V+), IC5.P$6 (OUT), IC6.P$8 (V+), IC7.P$2 (V+), IC8.P$12 (VCC), R6.1
+3V3: C5.1, C7.1, IC1.2 (3V3), IC4.P$6 (OUT), R11.1, R12.1, R13.2
/ADCIn: IC1.4 (SENSOR_VP), R7.2, U$15.P$2 (2)
/BOOT: IC1.25 (IO0), R13.1, R14.2
/BatIn: IC1.5 (SENSOR_VN), R8.1, R9.2
/CE: IC3.P$8 (OUTC), IC6.P$1 (NO1), U$7.P$2 (2)
/CTS: J1.6
/EN: IC1.3 (EN), R15.2
/OPA_OUT: C13.2, D4.C, D6.A, IC3.P$14 (OUTD), IC8.P$9 (IN+), R5.2, R7.1
/PWR+: J2.1, JP1.1 (A), P2.1, U1.3 (VBAT), U$3.P$1 (1)
/RE: IC3.P$9 (-INC), IC6.P$2 (COM1), U$7.P$1 (1)
/RTS: J1.2
/RXD: IC1.34 (RXD0), J1.4
/SCL: IC1.36 (IO22), IC2.P$7 (SCL), IC8.P$5 (SCL), R12.2
/SDA: IC1.33 (IO21), IC2.P$8 (SDA), IC8.P$6 (SDA), R11.2
/SIG+: IC3.P$12 (+IND), IC6.P$5 (NC2), IC7.P$6 (NO)
/SIG-: C13.1, D1.A, D3.C, IC3.P$13 (-IND), IC7.P$4 (NC), R5.1
/SwitchEl: IC1.31 (IO19), IC6.P$7 (IN1)
/SwitchIV: IC1.30 (IO18), IC6.P$3 (IN2), IC7.P$1 (IN)
/TXD: IC1.35 (TXD0), J1.5
/VCC_FTDI: J1.3
/WE: IC7.P$5 (COM), U$6.P$1 (1)
GND: BOOT1.1, C1.2, C2.2, C3.2, C4.2, C5.2, C6.2, C7.2, C8.2, C10.2, C12.2, C14.2, C15.2, C16.2, C17.2, C18.2, C19.2, C20.2, C21.2, EN1.1, IC1.1 (GND), IC1.15 (GND), IC1.38 (GND), IC1.39 (GND), IC2.P$3 (GND), IC2.P$4 (/LDAC), IC2.P$5 (/CLR), IC2.P$6 (ADDR), IC3.P$11 (V-), IC4.P$2 (GND), IC5.P$2 (GND), IC6.P$4 (GND), IC7.P$3 (GND), IC8.P$3 (A0), IC8.P$4 (GND), IC8.P$7 (GND), IC8.P$8 (REF-), IC8.P$10 (IN-), IC8.P$11 (GND), J1.1, J2.2, LED1.C, P1.2 (GND), P1.3 (SWITCH), P1.4_1, P1.4_2, R9.1, R16.2, U1.2 (VSS), U$3.P$2 (2), U$6.P$2 (2), U$15.P$1 (1)
unnamed: BOOT1.2, C20.1, R14.1
unnamed: C1.1, C2.1, IC4.P$1 (IN), IC4.P$3 (EN), IC5.P$1 (IN), IC5.P$3 (EN), JP1.2 (B), P2.COM, R8.2, R10.2
unnamed: C3.1, IC4.P$4 (BYP)
unnamed: C4.1, IC5.P$4 (BYP)
unnamed: C9.1, IC3.P$1 (OUTA), IC3.P$2 (-INA), R3.1
unnamed: C9.2, R1.2, R2.1
unnamed: C10.1, IC3.P$3 (+INA), R2.2
unnamed: C11.1, IC3.P$6 (-INB), IC3.P$7 (OUTB), IC3.P$10 (+INC)
unnamed: C11.2, R3.2, R4.1
unnamed: C12.1, IC3.P$5 (+INB), R4.2
unnamed: C14.1, IC8.P$2 (COMP)
unnamed: C15.1, IC8.P$1 (REFOUT)
unnamed: C21.1, EN1.2, R15.1
unnamed: D1.C, D2.A
unnamed: D2.C, D4.A
unnamed: D3.A, D5.C
unnamed: D5.A, D6.C
unnamed: IC2.P$1 (VOUT_A), R1.1
unnamed: IC2.P$2 (VOUT_B), IC6.P$6 (COM2)
unnamed: IC2.P$10 (REF), R6.2
unnamed: LED1.A, R10.1
unnamed: P1.1 (CENTER), P2.3, U1.1 (CEN), U1.4 (VDD)
unnamed: R16.1, U1.5 (PROG)

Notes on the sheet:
Digital
Analog
REF COUNTER
WORKING GND
R16: Charge current = 1000mA/value(kOhm). 10k=100mA (1000mA/10=100mA).

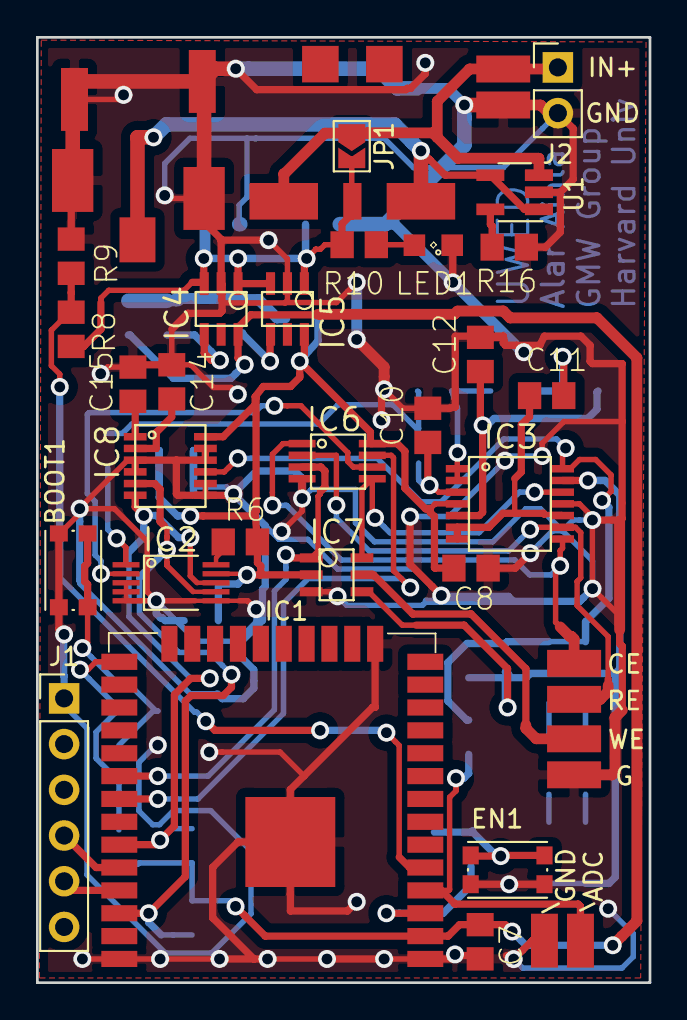
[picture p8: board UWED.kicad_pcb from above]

Board: 2 copper layers, 34.0 x 52.5 mm, 64 parts (0 on the bottom side), 43 nets.

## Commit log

2019-07-04 New project files with ESP-WROOM-32 and integrated charger chip - untested.
    [1719730004.stp, CUI_PJ-014CH-SMT-TR.step, CUI_PJ-032H-SMT-TR.step, KMR221GLFS.stp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]
2021-04-06 Added README, filled in BOM to provide order list for DIGIKEY
    [UWED2_proto.xlsx]
